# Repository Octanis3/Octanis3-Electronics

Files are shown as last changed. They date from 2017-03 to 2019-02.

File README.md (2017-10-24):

# Octanis3-Electronics

Contains PCB files of the Owl Monitoring Device. More information on http://nestbox.octanis.org/

## Folders
* *_admin*: General administrative documents (e.g. Sponsoring documents, Project proposals etc.)
* *Nestbox_v1*: First PCB version with Lighbarrier, 13MHz RFID, (untested) LORA module
* *Nextbox_v2*: Second PCB version using 125-134 kHz RFID

## Dependencies
* Created with KiCAD 4.0.4 stable
* BOM created with bom2groupedCsv.xsl plugin by Wolf Walter.
* Schematic parts managed with https://github.com/BPJWES/KiCAD_Partslist_editor

2017

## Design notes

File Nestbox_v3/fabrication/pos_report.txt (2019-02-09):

Info: Front side (top side) place file: '/Users/raffael/Desktop/Octanis/Octanis3/pcb/Nestbox_v2/fabrication/Nestbox_v2-top.pos'.
Info: Component count: 82.
Info: Back side (bottom side) place file: '/Users/raffael/Desktop/Octanis/Octanis3/pcb/Nestbox_v2/fabrication/Nestbox_v2-bottom.pos'.
Info: Component count: 4.
Info: Full component count: 86

Component Placement File generation OK.

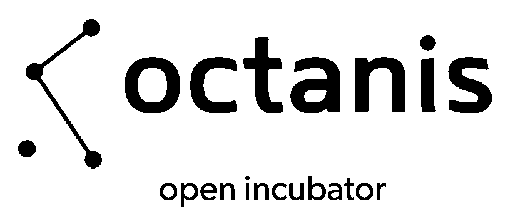
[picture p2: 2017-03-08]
_admin/octanis.bmp

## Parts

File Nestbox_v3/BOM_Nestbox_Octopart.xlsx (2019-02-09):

Item | Qty | Reference(s) | Value | LibPart | Footprint | SKU | NOTES
13 | 1 | CON301 | DEV-13712 | conn:Micro_SD_Card | Octanis3:MICRO-SD9+4P-SMD-16.1X14.5X1.85MM
14 | 1 | D301 | SMD-LED-CLEAR-YELLOW_0603_ | Nestbox_v2-cache:SMD-LED-CLEAR-GREEN_0603_ | SeeedOPL-LED-2016:LED-0603 | 304090043
15 | 1 | D302 | SMD-LED-CLEAR-BLUE_0603_ | Nestbox_v2-cache:SMD-LED-CLEAR-BLUE_0603_ | SeeedOPL-LED-2016:LED-0603 | 304090045
27 | 1 | L201 | 4.7uH | device:L | Inductors:Inductor_Taiyo-Yuden_NR-60xx_HandSoldering |  | consolidate with other inductor possible?
28 | 1 | L202 | 5uH | device:L | Inductors:Inductor_Taiyo-Yuden_NR-30xx |  | ??? Are the component names inverted???
29 | 1 | L301 | SMD-FERRITE-BEAD-2500R-50MA_0603_ | Nestbox_v2-cache:SMD-FERRITE-BEAD-2500R-50MA_0603_ | SeeedOPL-Inductor-2016:L0603 | 303030020
33 | 1 | Q201 | tph1r712mdl1q | device:Q_PMOS_DGS | Octanis3:TDSON-8-1_HandSoldering
34 | 2 | Q301, Q501 | NTR3A052PZT1G | device:Q_PMOS_GSD | TO_SOT_Packages_SMD:TSOT-23
35 | 2 | Q601, Q603 | DMG2301L-7 | device:Q_PMOS_GSD | TO_SOT_Packages_SMD:TSOT-23
36 | 2 | Q602, Q604 | DMG3402L | device:Q_NMOS_GSD | TO_SOT_Packages_SMD:TSOT-23
37 | 1 | Q701 | DMG3402L | device:Q_NMOS_GSD | TO_SOT_Packages_SMD:TSOT-23
56 | 1 | U201 | TPS62745 | Octanis3:TPS62745 | Octanis3:WSON_3x2mm_12pin |  | inductor too close.. Pads of tps not accessible
57 | 1 | U202 | LTC3534 | Octanis3:LTC3534 | SeeedOPL-IC-2016:SSOP16-0.635-5X4MM
58 | 1 | U203 | LP5907 | regul:LD3985M | texasinstruments:SOT23-5
59 | 1 | U301 | MSP430FR5969 | Octanis3:MSP430FR5969 | chips:S-PVQFN-N48
60 | 1 | U501 | ESP-12S | Octanis3:ESP-12S | Octanis3:ESP-12E_SMD_UART_ONLY
61 | 1 | U601 | ADS1220 | adc-dac:ADS1120-PW | Housings_SSOP:TSSOP-16_4.4x5mm_Pitch0.65mm
62 | 1 | Y301 | Crystal | device:Crystal | SeeedOPL-Crystal Oscillator-2016:X2-SMD-L2.0X1.2X0.55MM
 |  |  | SD CARD

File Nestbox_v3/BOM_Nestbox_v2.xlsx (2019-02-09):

Source: | /Users/raffael/Desktop/Octanis/Octanis3/pcb/Nestbox_v2/Nestbox_v2.sch
Date: | 2018 June 07, Thursday 10:21:40
Tool: | Eeschema 4.0.7
Generator: | /usr/local/Cellar/kicad/HEAD-19d5cc7/kicad.app/Contents/SharedSupport/plugins/bom_csv_grouped_by_value.py
Component Count: | 106
Item | Qty | Reference(s) | Value | LibPart | Footprint | Datasheet | MFG_PN | MFR_PN | MPN | Mouser-Part | SKU | NOTES
1 | 7 | C201, C203, C205, C206, C207, C304, C610 | 10u | device:C | Capacitors_SMD:C_0603 |  |  |  |  |  |  | Change to 805 size
2 | 5 | C202, C204, C601, C607, C608 | 1u | device:C | Capacitors_SMD:C_0603
3 | 1 | C208 | 330p | device:C | Capacitors_SMD:C_0603
4 | 1 | C209 | 10p | device:C | Capacitors_SMD:C_0603
5 | 1 | C210 | 33p | device:C | Capacitors_SMD:C_0603
6 | 4 | C301, C305, C308, C609 | 100n | device:C | Capacitors_SMD:C_0603
7 | 2 | C302, C303 | 25 pF | Nestbox_v2-cache:CERAMIC-12PF-50V-5%-NPO_0603_ | Capacitors_SMD:C_0603 |  |  |  | CC0603JRNPO9BN120 |  | 302010067 | rename; wrong MPN, is not in würth box. Used 24pf
8 | 1 | C306 | 100u | device:CP | Capacitors_SMD:C_0603 |  |  |  |  | 667-ECE-A0JKA101
9 | 1 | C307 | 0.1u | device:C | Capacitors_SMD:C_0603 |  |  |  |  |  |  | $
10 | 3 | C602, C603, C605 | 100n 1% | device:C | Capacitors_SMD:C_0603 |  |  |  |  |  |  | C602 label confusing position
11 | 2 | C604, C606 | 10n X2Y | Octanis3:C_X2Y | Octanis3:Capacitor_X2Y_603 |  |  |  |  |  |  | check land pattern with datasheet
12 | 1 | C611 | 10n | device:C | Capacitors_SMD:C_0603 |  |  |  |  |  |  | silkscreen illegible
13 | 1 | CON301 | Micro_SD_Card | conn:Micro_SD_Card | Octanis3:MICRO-SD9+4P-SMD-16.1X14.5X1.85MM
14 | 1 | D301 | SMD-LED-CLEAR-YELLOW_0603_ | Nestbox_v2-cache:SMD-LED-CLEAR-GREEN_0603_ | SeeedOPL-LED-2016:LED-0603 |  |  |  | 19-217-G7C-AN1P2-3T |  | 304090043
15 | 1 | D302 | SMD-LED-CLEAR-BLUE_0603_ | Nestbox_v2-cache:SMD-LED-CLEAR-BLUE_0603_ | SeeedOPL-LED-2016:LED-0603 |  |  |  | 19-217-BHC-ZL1M2RY-3T |  | 304090045
16 | 1 | J201 | BATT_CONN_01X02 | conn:CONN_01X02 | Terminal_Blocks:TerminalBlock_Pheonix_PT-3.5mm_2pol
17 | 1 | J401 | LB_DETECT_CONN_01X04 | conn:CONN_01X04 | Terminal_Blocks:TerminalBlock_Pheonix_MPT-2.54mm_4pol
18 | 1 | J402 | CONN_01X05 | conn:CONN_01X05 | Terminal_Blocks:TerminalBlock_Pheonix_MPT-2.54mm_5pol
19 | 1 | J501 | CONN_01X01 | conn:CONN_01X01 | Pin_Headers:Pin_Header_Straight_1x01_Pitch2.54mm
20 | 1 | J502 | CONN_01X06 | conn:CONN_01X06 | Pin_Headers:Pin_Header_Straight_1x06_Pitch2.54mm
21 | 1 | J601 | LOAD_CELL_CONN_01X04 | conn:CONN_01X04 | Terminal_Blocks:TerminalBlock_Pheonix_MPT-2.54mm_4pol
22 | 1 | J701 | RFID_CONN_01X05 | conn:CONN_01X05 | Terminal_Blocks:TerminalBlock_Pheonix_MPT-2.54mm_5pol
23 | 1 | JP201 | VAA_Jumper_SELECT_Dual | Octanis3:Jumper_SELECT_Dual | Pin_Headers:Pin_Header_Straight_1x03
24 | 1 | JP203 | Jumper_3V3 | device:Jumper | Pin_Headers:Pin_Header_Straight_1x02
25 | 1 | JP501 | Jumper | device:Jumper | Connect:GS2
26 | 1 | JP701 | V_RFID_Jumper_SELECT_Dual | Octanis3:Jumper_SELECT_Dual | Pin_Headers:Pin_Header_Straight_1x03_Pitch2.54mm
27 | 1 | L201 | 4.7uH | device:L | Inductors:Inductor_Taiyo-Yuden_NR-60xx_HandSoldering |  | XFL3010-472MEB
28 | 1 | L202 | 5uH | device:L | Inductors:Inductor_Taiyo-Yuden_NR-30xx |  |  | MSS7341-502NLD |  |  |  | ??? Are the component names inverted???
29 | 1 | L301 | SMD-FERRITE-BEAD-2500R-50MA_0603_ | Nestbox_v2-cache:SMD-FERRITE-BEAD-2500R-50MA_0603_ | SeeedOPL-Inductor-2016:L0603 |  |  |  |  |  | 303030020
30 | 1 | P301 | RX/TX | conn:CONN_01X02 | Socket_Strips:Socket_Strip_Straight_1x02_Pitch2.54mm
31 | 1 | P302 | TST/RST | conn:CONN_01X02 | Socket_Strips:Socket_Strip_Straight_1x02_Pitch2.54mm
32 | 1 | P303 | DEBUG_3V3 | conn:CONN_01X02 | Socket_Strips:Socket_Strip_Straight_1x02_Pitch2.54mm
33 | 1 | Q201 | tph1r712mdl1q | device:Q_PMOS_DGS | Octanis3:TDSON-8-1_HandSoldering
34 | 2 | Q301, Q501 | NTR3A052PZT1G | device:Q_PMOS_GSD | TO_SOT_Packages_SMD:TSOT-23
35 | 2 | Q601, Q603 | DMG2301L-7 | device:Q_PMOS_GSD | TO_SOT_Packages_SMD:TSOT-23
36 | 2 | Q602, Q604 | DMG3402L | device:Q_NMOS_GSD | TO_SOT_Packages_SMD:TSOT-23
37 | 1 | Q701 | DMG3402L | device:Q_NMOS_GSD | TO_SOT_Packages_SMD:TSOT-23
38 | 1 | R201 | 82k 1% | device:R | Resistors_SMD:R_0603 |  |  |  |  |  |  | consolidate
39 | 2 | R202, R701 | 47K 1% | device:R | Resistors_SMD:R_0603 |  |  |  |  |  |  | R701 could be 82k
40 | 1 | R203 | 10k | device:R | Resistors_SMD:R_0603
41 | 1 | R204 | 162k 1% | device:R | Resistors_SMD:R_0603
42 | 1 | R205 | 649k 1% | device:R | Resistors_SMD:R_0603
43 | 1 | R206 | 15k | device:R | Resistors_SMD:R_0603
44 | 1 | R301 | 47K | Nestbox_v2-cache:DIP-RES-47K-5%-1_4W_PR-D2.3XL6.5MM_ | Resistors_SMD:R_0603 |  |  |  | FHCFR-1_4W-473J |  | 301020022 | consolidate
45 | 6 | R303, R304, R305, R610, R611, R612 | 47R | device:R | Resistors_SMD:R_0603
46 | 2 | R306, R307 | 1K | device:R | Resistors_SMD:R_0603
47 | 8 | R308, R309, R501, R502, R503, R504, R505, R506 | 10K | device:R | Resistors_SMD:R_0603 |  |  |  |  |  |  | rename --> 10k
48 | 4 | R401, R402, R403, R404 | DNP | device:R | Resistors_SMD:R_0603
49 | 4 | R601, R602, R603, R604 | 1k 0.1% | device:R | Resistors_SMD:R_0603 |  |  |  | ERJ-PB3B1001V
50 | 2 | R605, R606 | 100R 1% | device:R | Resistors_SMD:R_0603 |  |  |  | ERA3AEB101V
51 | 2 | R607, R608 | 0R | device:R | Resistors_SMD:R_0603
52 | 1 | R609 | 2k2 | device:R | Resistors_SMD:R_0603 |  |  |  |  |  |  | could maybe be consolidated with LED resistor values
53 | 2 | R702, R703 | 47K 1% | device:R | Resistors_SMD:R_0603
54 | 2 | R704, R705 | 82k 1% | device:R | Resistors_SMD:R_0603
55 | 1 | SW301 | SMD-BUTTON_2P-3.0X2.5X1.2+0.4MM_ | Nestbox_v2-cache:SMD-BUTTON_2P-3.0X2.5X1.2+0.4MM_ | Buttons_Switches_SMD:SW_SPST_B3S-1000 |  |  |  | B3U-1000P-B |  | 311020047
56 | 1 | U201 | TPS62745 | Octanis3:TPS62745 | Octanis3:WSON_3x2mm_12pin |  |  |  |  |  |  | inductor too close.. Pads of tps not accessible
57 | 1 | U202 | LTC3534 | Octanis3:LTC3534 | SeeedOPL-IC-2016:SSOP16-0.635-5X4MM
58 | 1 | U203 | LP5907 | regul:LD3985M | texasinstruments:SOT23-5
59 | 1 | U301 | MSP430FR5969 | Octanis3:MSP430FR5969 | chips:S-PVQFN-N48 |  |  |  | MSP430FR5969IRGZR
60 | 1 | U501 | ESP-12S | Octanis3:ESP-12S | Octanis3:ESP-12E_SMD_UART_ONLY
61 | 1 | U601 | ADS1220 | adc-dac:ADS1120-PW | Housings_SSOP:TSSOP-16_4.4x5mm_Pitch0.65mm
62 | 1 | Y301 | Crystal | device:Crystal | SeeedOPL-Crystal Oscillator-2016:X2-SMD-L2.0X1.2X0.55MM |  |  |  | FC-12M 32.7680KA-A3
 |  |  |  |  |  |  |  |  | ECS-.327-12.5-12-TR
 |  |  | SD CARD |  |  |  |  |  | SDSDQAB-008G

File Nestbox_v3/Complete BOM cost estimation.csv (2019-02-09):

Qty | Line Item | Total Qty (@ Batch Size: 40) | Unit Price (@ Batch Size: 40) | Supplier | Total per device | Batch Total
 |  |  | Mouser
3 | C0805C102JAGACTU, | 120 | 0.1617 | Mouser | 0.49 | 19.40
2 | DMG2301L-7 | 80 | 0.2093 | Mouser | 0.42 | 16.75
1 | C0805C100KBRACTU, | 40 | 0.2619 | Mouser | 0.26 | 10.48
2 | DMG3402L-7 | 80 | 0.2748 | Mouser | 0.55 | 21.98
1 | DMG3402L-7 | 40 | 0.2748 | Mouser | 0.27 | 10.99
1 | C0805C182JAGACAUTO | 40 | 0.2778 | Mouser | 0.28 | 11.11
1 | C0805C152JBGACAUTO | 40 | 0.2788 | Mouser | 0.28 | 11.15
2 | NTR3A052PZT1G | 80 | 0.3085 | Mouser | 0.62 | 24.68
1 | LP5907MFX-3.0/NOPB | 40 | 0.4464 | Mouser | 0.45 | 17.86
1 | FC-12M 32.7680KA-A3 | 40 | 0.5704 | Mouser | 0.57 | 22.82
1 | MSS7341-502NLB | 40 | 1.2897 | Mouser | 1.29 | 51.59
1 | tph1r712mdl1q | 40 | 1.4286 | Mouser | 1.43 | 57.14
1 | XFL3010-472MEB | 40 | 1.7163 | Mouser | 1.72 | 68.65
1 | TPS62745DSSR | 40 | 1.7262 | Mouser | 1.73 | 69.05
1 | MSP430FR5969IRGZR | 40 | 4.1667 | Mouser | 4.17 | 166.67
1 | LTC3534EDHC#PBF | 40 | 6.2599 | Mouser | 6.26 | 250.40
1 | SDSDQAB-008G | 40 | 6.8948 | Mouser | 6.89 | 275.79
1 | ADS1220IPW | 40 | 8.8988 | Mouser | 8.90 | 355.95
1 | DEV-13712 | 40 | 14.8314 | Mouser | 14.83 | 593.25
1 | Passive Parts | 40 |  |  | 10.00 | 400.00
 |  | Total component value |  |  | 61.39 | 2455.72
 |  | SeeedStudio Markup (10%) |  |  | 6.14 | 245.57
 | Total component price (Seeedstudio) |  |  |  | 67.53 | 2701.29
1 | Wifi ESP-12S | 40 |  |  | 3.97 | 158.73
1 | YGX-SP3 | 40 |  | Alibaba | 22.00 | 880.00
2 | SensorCable | 80 |  | AliExpress | 9.00 | 360.00
1 | SonoffCase | 40 |  | AliExpress | 5.16 | 206.35
1 | EM4095HMSO16A | 40 |  |  | 3.00 | 120.00
1 | RFID Coil | 40 |  | Priority1Design | 5.50 | 220.20
1 | RFID Case | 40 |  | Aliexpress | 0.85 | 34.13
1 | AABatteryCase | 40 |  | Aliexpress | 1.03 | 41.27
1 | Nestbox PCB | 40 |  |  | 3.97 | 158.73
1 | RFID PCB | 40 |  |  | 2.98 | 119.05
1 | Mechanical Parts | 40 |  |  | 10.00 | 400.00
1 | Wood, MDF, LaserCutter | 40 |  |  | 5.00 | 200.00
1 | User Button | 40 |  |  | 0.99 | 39.68
1 | 4pc Battery LADDA | 40 |  | IKEA | 6.95 | 278.00
1 | PCB assembly | 40 |  |  | 39.68 | 1587.30
 | Total other parts value |  |  |  | 120.09 | 4803.43
 | VAT import fees (7.7%) |  |  |  | 9.25 | 369.86
 | Other import service fees, shipping and tariffs |  |  |  |  | 500.00
 | Total costs for electronics |  |  |  | 209.36 | 8374.59

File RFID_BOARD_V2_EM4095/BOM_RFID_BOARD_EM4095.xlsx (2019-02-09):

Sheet: RFID_BOARD_EM4095.csv
Source: | /Users/raffael/Desktop/Octanis/Octanis3/pcb/RFID_BOARD_V2_EM4095/RFID_BOARD_EM4095.sch
Date: | 2018 July 01, Sunday 18:29:10
Tool: | Eeschema 4.0.7
Generator: | /usr/local/Cellar/kicad/HEAD-19d5cc7/kicad.app/Contents/SharedSupport/plugins/bom_csv_grouped_by_value.py
Component Count: | 25
Individual Components:
Item | Qty | Reference(s) | Value | LibPart | Footprint | Datasheet | MPN
 |  | C1 | 10u | device:C | Capacitors_SMD:C_0805
 |  | C2 | 100n | device:C | Capacitors_SMD:C_0603
 |  | C3 | 1.8n 250V | device:C | Capacitors_SMD:C_0805 |  | C0805C182JAGAC
 |  | C4 | 1.8n 250V | device:C | Capacitors_SMD:C_0805 |  | C0805C182JAGAC
 |  | C5 | 10n (22n max) | device:C | Capacitors_SMD:C_0603
 |  | C6 | 10n | device:C | Capacitors_SMD:C_0603
 |  | C7 | 100n | device:C | Capacitors_SMD:C_0603
 |  | C8 | DNP or 100n | device:C | Capacitors_SMD:C_0603 | DNP
 |  | C9 | 100n 250V | device:C | Capacitors_SMD:C_0603
 |  | C10 | 100n 250V | device:C | Capacitors_SMD:C_0603
 |  | C11 | 100n | device:C | Capacitors_SMD:C_0603
 |  | C12 | 10u | device:C | Capacitors_SMD:C_0805
 |  | CRES1 | C_fine_tuning (10nF, 50V) | device:C | Capacitors_SMD:C_0603
 |  | CRES2 | 1.8n 250V | device:C | Capacitors_SMD:C_0805 |  | C0805C182JAGAC
 |  | CRES3 | 1n 450V | device:C | Capacitors_SMD:C_0805 |  | C0805C102JAGACTU or CC0805JKNPOBBN102
 |  | Cdiv1 | 10p 500V | device:C | Capacitors_SMD:C_0805 |  | C0805C100KBRACTU
 |  | Cdiv2 | 1.5n | device:C | Capacitors_SMD:C_0603
 |  | D1 | STTH1R06 | device:D | Diodes_SMD:SMB_Standard
 |  | J1 | CONN_01X05 | conn:CONN_01X05 | Pin_Headers:Pin_Header_Straight_1x05_Pitch2.54mm
 |  | J2 | CONN_01X01 | conn:CONN_01X01 | Measurement_Points:Measurement_Point_Square-SMD-Pad_Small
 |  | J3 | CONN_01X01 | conn:CONN_01X01 | Measurement_Points:Measurement_Point_Square-SMD-Pad_Small
 |  | R1 | 100R | device:R | Resistors_SMD:R_0603
 |  | R2 | 100k | device:R | Resistors_SMD:R_0603
 |  | R3 | 0R | device:R | Resistors_SMD:R_0603
 |  | U1 | EM4095 | Octanis3:EM4095 | Housings_SOIC:SOIC-16_3.9x9.9mm_Pitch1.27mm
Collated Components:
Item | Qty | Reference(s) | Value | LibPart | Footprint | Datasheet | MPN | assembly notes
1 | 2 | C1, C12 | 10u | device:C | Capacitors_SMD:C_0805 |  |  | c1 c11 part value exchanged
2 | 4 | C2, C7, C8, C11 | 100n | device:C | Capacitors_SMD:C_0603 |  |  | C8 must be precise! The rest is decoupling
3 | 3 | C3, C4, CRES2 | 1.8n 250V | device:C | Capacitors_SMD:C_0805 |  | C0805C182JAGAC
4 | 2 | C5, C6 | 10n | device:C | Capacitors_SMD:C_0603 |  |  | C5 can be max. 22n
8 | 1 | CRES1 | C_fine_tuning (10nF, 50V) | device:C | Capacitors_SMD:C_0603 |  |  | placed 10n from würth --> Target frequency ca. 124-125 kHz
7 | 2 | C9, C10 | 100n 250V | device:C | Capacitors_SMD:C_0603 |  | C2012X7T2E104K125AA | should be 0805 footprint!!!
9 | 1 | CRES3 | 1n 450V | device:C | Capacitors_SMD:C_0805 |  | C0805C102JAGACTU or CC0805JKNPOBBN102
10 | 1 | Cdiv1 | 10p 500V | device:C | Capacitors_SMD:C_0805 |  | C0805C100KBRACTU
11 | 1 | Cdiv2 | 1.5n | device:C | Capacitors_SMD:C_0603 |  | C0805C152JBGACAUTO
12 | 1 | D1 | STTH1R06 | device:D | Diodes_SMD:SMB_Standard
15 | 1 | R1 | 100R | device:R | Resistors_SMD:R_0603
16 | 1 | R2 | 100k | device:R | Resistors_SMD:R_0603
17 | 1 | R3 | 0R | device:R | Resistors_SMD:R_0603
2 left!!! | 1 | U1 | EM4095 | Octanis3:EM4095 | Housings_SOIC:SOIC-16_3.9x9.9mm_Pitch1.27mm

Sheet: FINAL VERSION
Item | Qty | Reference(s) | Value | LibPart | Footprint | Datasheet | MPN | assembly notes |  | capacitor choice (nF)
1 | 2 | C1, C12 | 10u | device:C | Capacitors_SMD:C_0805 |  | GRM21BR61E106MA73L |  | Inductor value | 2.8 | 2.56 | 2.56 | 2.56 | 2.56
2 | 4 | C2, C7, C8, C11 | 100n | device:C | Capacitors_SMD:C_0603 |  | GCM188L81H104KA57D | C8 must be precise! The rest is decoupling | res3 | 1 | 1 | 1.1 | 1 | 1
 |  | C8 | 100n 1%
3 | 1 | CRES2 | 1.8n 250V | device:C | Capacitors_SMD:C_0805 |  | C0805C182JAGAC |  | res2 | 1.8 | 1.8 | 1.6 | 1.8 | 1.8
4 | 2 | C5, C6 | 10n | device:C | Capacitors_SMD:C_0603 |  | CGA3E1C0G2A103J080AC | C5 can be max. 22n, alternative: GRM1885C1H103JA01D | res1 | 10 | 10 | 10 | 15 | 68
5 | 1 | CRES1 | 12nF | device:C | Capacitors_SMD:C_0603 |  | VJ0603Y153JXAAC (https://www.mouser.ch/ProductDetail/Vishay-Vitramon/VJ0603Y153JXAAC?qs=sGAEpiMZZMs0AnBnWHyRQKubRBCdVSJlEvhtpSFB550%3d) | 15n alternative: VJ0603Y153JXAAC | f_res (kHz) | 122.3807176 | 127.9888181 | 127.1564094 | 126.6937883 | 124.6482345
6 | 1 | CRES3 | 1n 450V | device:C | Capacitors_SMD:C_0805 |  | CC0805JKNPOBBN102 | (C0805C102JAGACTU or CC0805JKNPOBBN102)
7 | 1 | Cdiv1 | 10p 500V | device:C | Capacitors_SMD:C_0805 |  | C0805C100KBRACTU
8 | 1 | Cdiv2 | 1.5n | device:C | Capacitors_SMD:C_0603 |  | C0805C152JBGACAUTO
9 | 1 | R3 | 0R | device:R | Resistors_SMD:R_0603
10 | 1 | U1 | EM4095 | Octanis3:EM4095 | Housings_SOIC:SOIC-16_3.9x9.9mm_Pitch1.27mm

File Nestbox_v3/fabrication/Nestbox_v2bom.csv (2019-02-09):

Id | Designator | Package | Quantity | Designation | Supplier and ref
1 | FID3,FID2,FID1 | Fiducial_1mm_Dia_2.54mm_Outer_CopperTop | 3 | Fiducial_1mm_Dia_2.54mm_Outer_CopperTop
2 | R304,R303,R305,R610,R611,R612 | R_0603 | 6 | 47R
3 | REF**,REF**,REF** | MountingHole_2.5mm | 3 | MountingHole_2.5mm
4 | C201,C203,C205,C206,C207,C304,C610 | C_0603 | 7 | 10u
5 | C202,C204,C601,C607,C608 | C_0603 | 5 | 1u
6 | C301,C305,C308,C609 | C_0603 | 4 | 100n
7 | C302,C303 | C_0603 | 2 | 25 pF
8 | C306 | C_0603 | 1 | 100u
9 | C307 | C_0603 | 1 | 0.1u
10 | C602,C603,C605 | C_0603 | 3 | 100n 1%
11 | C611 | C_0603 | 1 | 10n
12 | D301 | LED-0603 | 1 | SMD-LED-CLEAR-GREEN_0603_
13 | D302 | LED-0603 | 1 | SMD-LED-CLEAR-BLUE_0603_
14 | J201 | TerminalBlock_Pheonix_PT-3.5mm_2pol | 1 | BATT_CONN_01X02
15 | JP203 | Pin_Header_Straight_1x02 | 1 | Jumper_3V3
16 | JP701 | Pin_Header_Straight_1x03_Pitch2.54mm | 1 | V_RFID_Jumper_SELECT_Dual
17 | L301 | L0603 | 1 | SMD-FERRITE-BEAD-2500R-50MA_0603_
18 | P301 | Socket_Strip_Straight_1x02_Pitch2.54mm | 1 | RX/TX
19 | P302 | Socket_Strip_Straight_1x02_Pitch2.54mm | 1 | TST/RST
20 | R201 | R_0603 | 1 | 100k
21 | R202,R701 | R_0603 | 2 | 50k
22 | R203 | R_0603 | 1 | 10k
23 | R204 | R_0603 | 1 | 162k
24 | R205 | R_0603 | 1 | 649k
25 | R301 | R_0603 | 1 | 47K
26 | R306,R307 | R_0603 | 2 | 1K
27 | R308,R309,R501,R502,R503,R504,R505,R506 | R_0603 | 8 | 10K
28 | R601,R602,R603,R604 | R_0603 | 4 | 1k 1%
29 | R605,R606 | R_0603 | 2 | 100R 1%
30 | R607,R608 | R_0603 | 2 | 0R
31 | R609 | R_0603 | 1 | 2k2
32 | R702,R703 | R_0603 | 2 | 18k
33 | R704,R705 | R_0603 | 2 | 33k
34 | SW301 | SW_SPST_B3S-1000 | 1 | SMD-BUTTON_2P-3.0X2.5X1.2+0.4MM_
35 | U203 | SOT23-5 | 1 | LP5907
36 | U301 | S-PVQFN-N48 | 1 | MSP430FR5969
37 | U601 | TSSOP-16_4.4x5mm_Pitch0.65mm | 1 | ADS1220
38 | Y301 | X2-SMD-L2.0X1.2X0.55MM | 1 | Crystal
39 | JP201 | Pin_Header_Straight_1x03 | 1 | VAA_Jumper_SELECT_Dual
40 | P303 | Socket_Strip_Straight_1x02_Pitch2.54mm | 1 | DEBUG_3V3
41 | C208 | C_0603 | 1 | 330p
42 | C209 | C_0603 | 1 | 10p
43 | C210 | C_0603 | 1 | 33p
44 | L201 | Inductor_Taiyo-Yuden_NR-60xx_HandSoldering | 1 | 4.7uH
45 | L202 | Inductor_Taiyo-Yuden_NR-30xx | 1 | 5uH
46 | R206 | R_0603 | 1 | 15k
47 | U202 | SSOP16-0.635-5X4MM | 1 | LTC3534
48 | J501 | Pin_Header_Straight_1x01_Pitch2.54mm | 1 | CONN_01X01
49 | R401,R402,R403,R404 | R_0603 | 4 | DNP
50 | J401 | TerminalBlock_Pheonix_MPT-2.54mm_4pol | 1 | LB_DETECT_CONN_01X04
51 | J402 | TerminalBlock_Pheonix_MPT-2.54mm_5pol | 1 | CONN_01X05
52 | J601 | TerminalBlock_Pheonix_MPT-2.54mm_4pol | 1 | LOAD_CELL_CONN_01X04
53 | J701 | TerminalBlock_Pheonix_MPT-2.54mm_5pol | 1 | RFID_CONN_01X05
54 | J502 | Pin_Header_Straight_1x06_Pitch2.54mm | 1 | CONN_01X06
55 | Q601,Q603 | TSOT-23 | 2 | DMG2301L-7
56 | U501 | ESP-12E_SMD_UART_ONLY | 1 | ESP-12S
57 | Q602,Q604 | TSOT-23 | 2 | DMG3402L
58 | JP501 | GS2 | 1 | Jumper
59 | C604,C606 | Capacitor_X2Y_603 | 2 | 10n X2Y
60 | Q201 | TDSON-8-1_HandSoldering | 1 | Q_PMOS_DGS
61 | CON301 | MICRO-SD9+4P-SMD-16.1X14.5X1.85MM | 1 | Micro_SD_Card
62 | U201 | WSON_3x2mm_12pin | 1 | TPS62745
63 | G*** | octanis3_logo | 1 | LOGO
64 | G*** | VogelwarteLogo3 | 1 | LOGO
65 | G*** | octanis_open_incubator_logo | 1 | LOGO
66 | REF*** | OSHW-Logo2_9.8x8mm_SilkScreen | 1 | OSHW-Logo2_9.8x8mm_SilkScreen
67 | Q301,Q501 | TSOT-23 | 2 | NTR3A052PZT1G
68 | Q701 | TSOT-23 | 1 | Q_NMOS_GSD

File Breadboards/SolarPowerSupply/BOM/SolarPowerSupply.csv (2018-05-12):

Reference | Quantity | Value | Footprint | Datasheet | MPN | Tolerance
BT101 | 1 | Battery | Octanis3:TE_282834-2 |  | 571-282834-2
C101 | 1 | 4.7u | Octanis3:C_SMD_2012_Hand |  | 81-GRM21R61A475KE34D | 10%
C102 | 1 | 100n | Capacitors_SMD:C_0603_HandSoldering
C103 | 1 | 10n | Capacitors_SMD:C_0603_HandSoldering |  |  | 10%
C104 C105 C106 C107 C108 C109 | 6 | 10u | Octanis3:C_SMD_2012_Hand |  | 81-GRM21BR61C106KE5K
C110 | 1 | 10p | Capacitors_SMD:C_0603_HandSoldering
D101 D102 | 2 | LED | LEDs:LED_0603_HandSoldering
JP101 JP102 JP103 JP104 JP105 | 5 | Jumper | Pin_Headers:Pin_Header_Straight_1x02_Pitch2.54mm
L101 | 1 | 22u | Inductors_SMD:L_Wuerth_WE-TPC-3816 |  | 710-744031220 | 20%
L102 L103 | 2 | 1.5u | Octanis3:L_2520_HandSoldering |  | 81-1269AS-H-1R5MP2
P101 | 1 | CONN_01X04 | Pin_Headers:Pin_Header_Straight_1x04_Pitch2.54mm
P102 | 1 | CONN_01X07 | Pin_Headers:Pin_Header_Straight_1x07_Pitch2.54mm
R101 | 1 | 1.69M | Resistors_SMD:R_0603_HandSoldering |  | 71-CRCW06031M69FKEA | 1%
R102 | 1 | 0.576M | Resistors_SMD:R_0603_HandSoldering |  | 71-CRCW0603-576K-E3 | 1%
R103 | 1 | 9.09M | Resistors_SMD:R_0603_HandSoldering |  | 71-CRCW06039M09FKEA | 1%
R104 | 1 | 6.04M | Resistors_SMD:R_0603_HandSoldering |  | 71-CRCW06036M04FKEA | 1%
R105 R114 R115 | 3 | 5.36M | Resistors_SMD:R_0603_HandSoldering |  | 71-CRCW06035M36FKEA | 1%
R106 | 1 | 5.9M | Resistors_SMD:R_0603_HandSoldering |  | 71-CRCW06035M90FKEA | 1%
R107 | 1 | 0E | Resistors_SMD:R_1206_HandSoldering
R108 | 1 | 4.12M | Resistors_SMD:R_0603_HandSoldering |  | 71-CRCW06034M12FKEA | 1%
R109 | 1 | 4.42M | Resistors_SMD:R_0603_HandSoldering |  | 71-CRCW06034M42FKEA | 1%
R110 | 1 | 3.65M | Resistors_SMD:R_0603_HandSoldering |  | 71-CRCW0603-3.65M-E3 | 1%
R111 R112 | 2 | 4.53M | Resistors_SMD:R_0603_HandSoldering |  | 71-CRCW06034M53FKEA | 1%
R113 | 1 | 0E | Resistors_SMD:R_0603_HandSoldering
R116 | 1 | DNP | Resistors_SMD:R_0603_HandSoldering
R117 R118 | 2 | R | Resistors_SMD:R_0603_HandSoldering
R119 R120 | 2 | 1M | Resistors_SMD:R_0603_HandSoldering |  | 71-CRCW06031M10JNEA
R121 | 1 | 1.1M | Resistors_SMD:R_0603_HandSoldering |  | 71-CRCW06031M10JNEA | 1%
R122 | 1 | 205k | Resistors_SMD:R_0603_HandSoldering |  | 71-CRCW0603-205K-E3 | 1%
SC101 | 1 | Solar_Cells | Octanis3:TE_282834-2 |  | 571-282834-2
U101 | 1 | bq25504 | Housings_DFN_QFN:QFN-16-1EP_3x3mm_Pitch0.5mm |  | 595-BQ25504RGTT
U102 | 1 | TPS63051 | Octanis3:VQFN_12_2.5x2.5mm |  | 595-TPS63051RMWT
U103 | 1 | TPS63050 | Octanis3:VQFN_12_2.5x2.5mm |  | 595-TPS63050RMWR

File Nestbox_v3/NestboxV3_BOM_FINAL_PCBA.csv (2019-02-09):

Reference(s) | MPN | Qty | MouserLink
C201, C203, C205, C206, C207, C304, C610 | CC0805KKX5R8BB106 | 7
C202, C204, C601, C607, C608 | CC0603KRX7R8BB105 | 5
C208 | CC0603JRNPO9BN331 | 1
C209 | CC0603JRNPO9BN100 | 1
C210 | CC0603JRNPO9BN330 | 1
C301, C305, C307, C308, C609 | CC0603KRX7R9BB104 | 5
C302, C303 | CC0603JRNPO9BN250 | 2 | https://www.mouser.ch/ProductDetail/Yageo/CC0603JRNPO9BN250
C306 | 293D107X0016D2TE3 | 1
C602, C603 | CC0603JRX7R7BB104 | 2
C611 | CC0603KRX7R9BB103 | 1
D301 | 19-217-G7C-AN1P2-3T | 1
D302 | 19-217-BHC-ZL1M2RY-3T | 1
L201 | MSS7341-502NLD | 1
L202 | XFL3010-472MEB | 1
L301 | BLM18AG121SN1D | 1
Q201 | TPH1R712MDL1Q | 1 | https://www.mouser.ch/ProductDetail/Toshiba/TPH1R712MDL1Q
Q301, Q501 | NTR3A052PZT1G | 2
Q701 | DMG3402L-7 | 1
R201, R207, R208, R302, R507, R701, R704, R705 | RC0603FR-0782KL | 8
R202, R702, R703 | RC0603FR-0747KL | 3
R203, R308, R309, R501, R503, R504, R505, R506 | RC0603JR-0710KL | 8
R204 | RC0603FR-07162KL | 1
R205 | RC0603FR-07649KL | 1
R206 | RC0603JR-0715KL | 1
R301 | RC0603FR-0747KL | 1
R303, R304, R603, R604 | RC0603JR-070RL | 4
R306, R307 | RC0603FR-071KL | 2
R605, R606 | RC0603FR-07100RL | 2
R610, R611, R612 | RC0603JR-0747RL | 3
SW301 | DTSM-62K-S-V-T/R(SN431) | 1
U201 | TPS62745DSSR | 1
U202 | LTC3534EDHC#PBF | 1
U203 | LP5907MFX-3.0/NOPB | 1
U301 | MSP430FR5969IRGZR | 1
U501 | ESP-12F | 1
U601 | ADS1220IPW | 1
Y301 | FC-12M 32.7680KA-A3 | 1

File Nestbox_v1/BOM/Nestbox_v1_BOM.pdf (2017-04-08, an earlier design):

Reference | Quantity | Value | Footprint
ANT_UHF1 | | 1 ANTENNA-CONN-U-FL_3P_ | SeeedOPL-Connector-2016:U-FL3P-SMD-2.6X2.6X1.0MM
BT1 | | 1 Battery | Connectors_Molex:Molex_KK-6410-02_02x2.54mm_Straight
C10 C14 | | 2 CERAMIC-1UF-25V-10%-X7R_0603_ | SeeedOPL-Capacitor-2016:C0603
C12 C13 | | 2 180pF | SeeedOPL-Capacitor-2016:C0603
C15 C16 | | 2 DNP | SeeedOPL-Capacitor-2016:C0603
C11 C17 | | 2 CERAMIC-10NF-50V-10%-X7R_0603_ | SeeedOPL-Capacitor-2016:C0603
C19 C22 | | 2 82pF | SeeedOPL-Capacitor-2016:C0402
C20 C21 C25 | | 3 DNP | Capacitors_SMD:C_0603
C23 C24 | | 2 150 pF | Capacitors_SMD:C_0603
C27 C28 | | 2 CERAMIC-22UF-6.3V-20%-X5R_0805_ | SeeedOPL-Capacitor-2016:C0805
C2 C3 | | 2 CERAMIC-12PF-50V-5%-NPO_0603_ | SeeedOPL-Capacitor-2016:C0603
C26 C4 | | 2 CERAMIC-10UF-25V-10%-X5R_0805_ | SeeedOPL-Capacitor-2016:C0805
C1 C18 C29 C5 C9 | | 5 CERAMIC-100NF-50V-10%-X7R_0603_ | SeeedOPL-Capacitor-2016:C0603
C6 C8 | | 2 CERAMIC-10PF-50V-5%-NPO_0603_ | SeeedOPL-Capacitor-2016:C0603
C7 | | 1 CERAMIC-1NF-50V-10%-X7R_0603_ | SeeedOPL-Capacitor-2016:C0603
D1 | | 1 SFH 4646 | Octanis3:MIDLED
D2 | | 1 SMD-LED-CLEAR-GREEN_0603_ | SeeedOPL-LED-2016:LED-0603
D3 | | 1 SMD-LED-CLEAR-BLUE_0603_ | SeeedOPL-LED-2016:LED-0603
FI1 | | 1 NFM18PS105R0J3D | murata-filter:NFM18PS
JP1 JP2 | | 2 JUMPER | Socket_Strips:Socket_Strip_Straight_1x02
L1 | 1 SMD-FERRITE-BEAD-2500R-50MA_0603_ SeeedOPL-Inductor-2016:L0603
L2 L5 | 2 | 742792042 Resistors_SMD:R_0805
L3 L4 | | 2 560nH | Resistors_SMD:R_0805
L6 | 1 | 742792093 Resistors_SMD:R_0805
L7 | | 1 XFL4020-102ME | Octanis3:XFL4020
P1 | | 1 RX/TX | Socket_Strips:Socket_Strip_Straight_1x02
P2 | | 1 TST/RST | Socket_Strips:Socket_Strip_Straight_1x02
P3 | | 1 VDD/GND | Socket_Strips:Socket_Strip_Straight_1x02
P4 | | 1 NFC_PWR_SEL | Socket_Strips:Socket_Strip_Straight_1x03
PB1 | | 1 LIGHT_BARRIER1 | Socket_Strips:Socket_Strip_Straight_1x02
PB2 | | 1 LIGHT_BARRIER2 | Socket_Strips:Socket_Strip_Straight_1x02
Q1 Q2 | | 2 SFH 3605 | Octanis3:MIDLED_phototransistor
R1 | | 1 SMD-RES-220R-5%-1_10W_0603_
R10 R13 R14 R18 | | 4 SMD-RES-0R-5%-1_10W_0603_ | SeeedOPL-Resistor-2016:R0603
R12 R15 R17 R2 R23 R28 R29 R3 R4 R9 | | 10 DNP | Resistors_SMD:R_0603
R11 R16 R19 R20 R8 | | 5 SMD-RES-3.3K-1%-1_10W_0603_ | SeeedOPL-Resistor-2016:R0603
R21 R22 | | 2 SMD-RES-330R-1%-1_10W_0603_ | SeeedOPL-Resistor-2016:R0603
R24 | | 1 SMD-RES-560K-5%-1_10W_0603_ | SeeedOPL-Resistor-2016:R0603
R25 | | 1 180k | Resistors_SMD:R_0603
R27 | | 1 47K | SeeedOPL-Resistor-2016:R0603
R5 R6 | | 2 SMD-RES-1K-5%-1_10W_0603_ | SeeedOPL-Resistor-2016:R0603
R26 R30 R7 | | 3 SMD-RES-10K-1%-1_10W_0603_ | SeeedOPL-Resistor-2016:R0603
RV1 RV2 | | 2 POT:2K | pot:3223G
SW1 | 1 SMD-BUTTON_2P-3.0X2.5X1.2+0.4MM_ SeeedOPL-Switch-2016:SW2-2.6-3.0X2.5X1.2+0.4MM
U1 | | 1 MSP430FR5969 | chips:S-PVQFN-N48
U2 | | 1 ST95HF | Octanis3:VFQFPN32
U3 | | 1 TPS630250RNC | Octanis3:RNC0014A
U4 | | 1 RN2483 | Octanis3:RN2483
Y1 | | 1 Crystal | SeeedOPL-Crystal Oscillator-2016:X2-SMD-L2.0X1.2X0.55MM
Y2 | | 1 ABM11-142-27.120MHz | Octanis3:Crystal_ABM11-142
ant1 | | 1 NFC_antenna | Octanis3:NFC_ANTENNA_CIRC

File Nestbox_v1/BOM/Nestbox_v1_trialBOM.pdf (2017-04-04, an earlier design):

Reference | Value | Footprint | MPN | SKU
D1 | SFH 4646 | Octanis3:MIDLED | 720-SFH4646Z
R1 | 100 Ohm, but also try higher values | SeeedOPL-Resistor-2016:R0603 | RC0603JR-07100RL | 301010090
R2 | DNP | Resistors_SMD:R_0603
Q1 | SFH 3605 | Octanis3:MIDLED_phototransistor | SFH 3605-Z
R4 | DNP | Resistors_SMD:R_0603
RV1 | 2k Trimmer | pot:3223G | 3313J-1-201E
R3 | DNP | Resistors_SMD:R_0603
Q2 | SFH 3605 | Octanis3:MIDLED_phototransistor | SFH 3605-Z
R28 | DNP | Resistors_SMD:R_0603
RV2 | 2k Trimmer or higher | pot:3223G | 3313J-1-201E
R29 | DNP | Resistors_SMD:R_0603
L3 | 0 Ohm | Resistors_SMD:R_0805 | CV201210-R56K
L4 | 0 Ohm | Resistors_SMD:R_0805 | CV201210-R56K
R21 | 330 Ohm | SeeedOPL-Resistor-2016:R0603 | RC0603FR-07330RL | 301010300
R22 | 330 Ohm | SeeedOPL-Resistor-2016:R0603 | RC0603FR-07330RL | 301010300
C12 | DNP | SeeedOPL-Capacitor-2016:C0603 | CC0603JRNPO9BN101 | 302010076
C13 | DNP | SeeedOPL-Capacitor-2016:C0603 | CC0603JRNPO9BN101 | 302010076
C15 | DNP | SeeedOPL-Capacitor-2016:C0603 | CC0603JRNPO9BN101 | 302010076
C16 | DNP | SeeedOPL-Capacitor-2016:C0603 | CC0603JRNPO9BN101 | 302010076
C19 | 150pF | SeeedOPL-Capacitor-2016:C0402 | CC0402JRNPO9BN470 | 302010007
C22 | 150pF | SeeedOPL-Capacitor-2016:C0402 | CC0402JRNPO9BN470 | 302010007

## Light barrier test

## Matching network variant 1: according to guided example

C21 | DNP | Capacitors_SMD:C_0603
C20 | DNP | Capacitors_SMD:C_0603
C24 | 15 pF | Capacitors_SMD:C_0603
C25 | DNP | Capacitors_SMD:C_0603
C23 | 220 pF | Capacitors_SMD:C_0603 | GQM1875C2E820JB12D
R23 | DNP | Resistors_SMD:R_0603
ant1 | NFC_antenna | Octanis3:NFC_ANTENNA_CIRC
L3 | 560nH (part number 742792042) | Resistors_SMD:R_0805 | CV201210-R56K or 742792042)
L4 | 560nH (part number 742792042) | Resistors_SMD:R_0805 | CV201210-R56K or 742792042)
R21 | 330 Ohm | SeeedOPL-Resistor-2016:R0603 | RC0603FR-07330RL | 301010300
R22 | 330 Ohm | SeeedOPL-Resistor-2016:R0603 | RC0603FR-07330RL | 301010300
C12 | 180 pF | SeeedOPL-Capacitor-2016:C0603 | CC0603JRNPO9BN101 | 302010076
C13 | 180 pF | SeeedOPL-Capacitor-2016:C0603 | CC0603JRNPO9BN101 | 302010076
C15 | DNP | SeeedOPL-Capacitor-2016:C0603 | CC0603JRNPO9BN101 | 302010076
C16 | DNP | SeeedOPL-Capacitor-2016:C0603 | CC0603JRNPO9BN101 | 302010076
C19 | 82pF | SeeedOPL-Capacitor-2016:C0402 | CC0402JRNPO9BN470 | 302010007
C22 | 82pF | SeeedOPL-Capacitor-2016:C0402 | CC0402JRNPO9BN470 | 302010007
C21 | DNP | Capacitors_SMD:C_0603
C20 | DNP | Capacitors_SMD:C_0603
C24 | 150 pF | Capacitors_SMD:C_0603
C25 | DNP | Capacitors_SMD:C_0603
C23 | 150 pF | Capacitors_SMD:C_0603 | GQM1875C2E820JB12D
R23 | DNP | Resistors_SMD:R_0603
ant1 | NFC_antenna | Octanis3:NFC_ANTENNA_CIRC

## Matching network variant 2: similar to Demo board

"DNP" = Do not place

## Explanations

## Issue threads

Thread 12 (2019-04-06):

### ISSUE TITLE
Next version PCB

### ISSUE THREAD

**Issue by traffael** [Octanis3/Octanis3-Electronics#12]
This issue summarizes the anticipated changes to the board for the next version.

+ larger MSP430 (e.g. FR5964) with maximum possible FRAM size for longer storage periods.
+ battery monitoring possibility (i.e. analog readout of the voltage)
- remove FI1 and replace with an alternative, less fragile filter part
- larger button

**Comment by traffael** [comment]
+ change IR receiver to something like this: TSOP75338WTR (TV remote IR receiver)

**Comment by deragent** [comment]
Design of v2 of Nestbox PCB is in progress (on branch Nestbox_v2). 

Will incorporate most of these changes proposed here.

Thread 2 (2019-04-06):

### ISSUE TITLE
Assemble & Test v1 PCB

### ISSUE THREAD

**Issue by traffael** [Octanis3/Octanis3-Electronics#2]

**Comment by traffael** [comment]
Done testing:
- general microcontroller functionality/flashing/blink/...
- SPI communication between uC and RFID chip
- RFID communication (UID readout from card) with read range up to 5 cm with smartcard
- on/off IR LED and photodetector

TO DO:
- determine good intensity of IR LED and practical readout voltages of the phototransistor
- test read range with real bird ring & adjust matching network if needed
- Power supply (DC-DC converter from battery voltage to 3.3V)

In general, v1 seems to be usable for testing in the real context!

**Comment by deragent** [comment]
So after some more extended testing things do not look so good anymore:
- Light Barrier was changed to use a  TSOP38238 for the receive side. This works very stable now in our Lab tests!
- The RFID communication was implemented and worked in general, but the system is very unstable and after some time (minutes) leads to system resets. Often after these resets the RFID chip stops working altogether. It often starts working again after re-soldering it or just heating it. We do not really know the source of these problems.
- The read range using bird tags is also very disappointing when it works, being on the order of 2-3 cm within the axis of the antenna, and basically 0 cm when not in the axis of the antenna.
- The DC/DC circuit is not working correctly at the moment. Given that the design was previously used in other projects this is most likely due to assembly problems (soldering etc).

The current strategy is to make some prototypes usable just having the light-barrier and storing the passages locally.
We also started working on a v2 prototype using 125kHz RFID instead of 13.65MHz.

**Comment by traffael** [comment]
done

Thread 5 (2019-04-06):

### ISSUE TITLE
Assembly of second light barrier

### ISSUE THREAD

**Issue by traffael** [Octanis3/Octanis3-Electronics#5]
(could use the same v1 PCB and only mound phototransistor & LED and connect it to the fully mounted reader PCB)

**Comment by deragent** [comment]
I would actually propose the second light barrier directly on the same PCB but on the other side! 
So the same position as the other light barrier but just on the lower side of the PCB. In order to not get interference between the two light barriers we can also switch the diode and the transistor on one side.

Given that this version is a prototype, I think it would be a good idea to put this directly in the design. We can still add a connector and some 0-Ohm resistors to disable this second light barrier and use an external one.
But I think to detect the passing and direction of a bird the proposed solution with two barriers just next to each other should work.

**Comment by traffael** [comment]
have added a second phototransistor on the backside (it is presumably enough to have just one light source). the thickness of the PCB is probably not enough though to detect a difference in time when one or the other barrier was interrupted.

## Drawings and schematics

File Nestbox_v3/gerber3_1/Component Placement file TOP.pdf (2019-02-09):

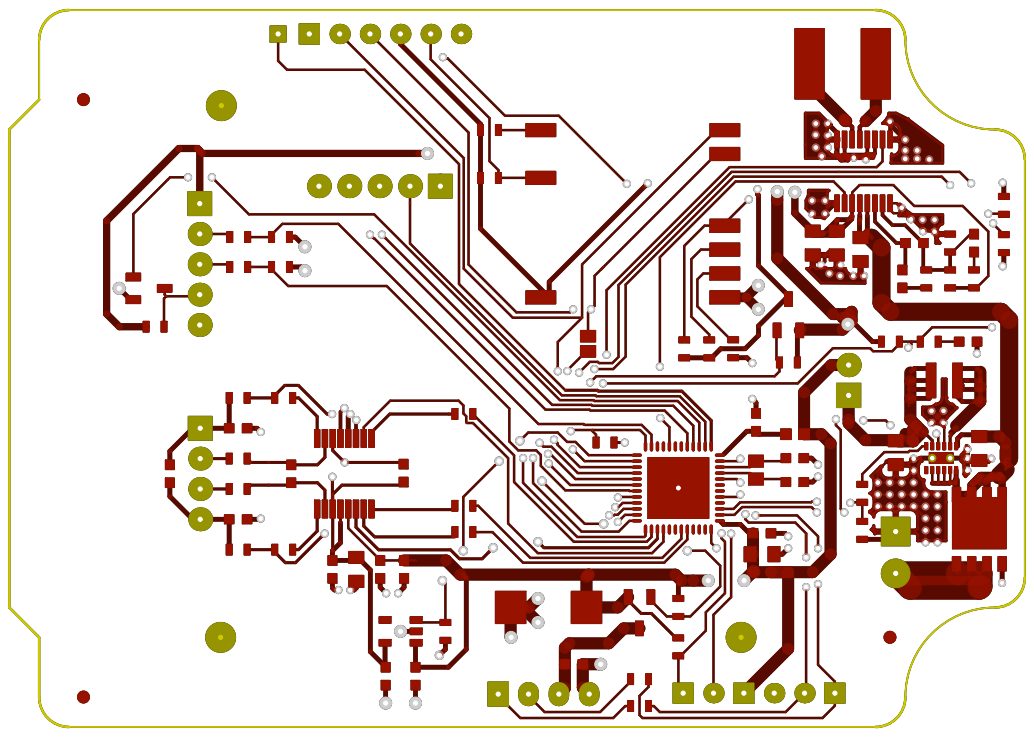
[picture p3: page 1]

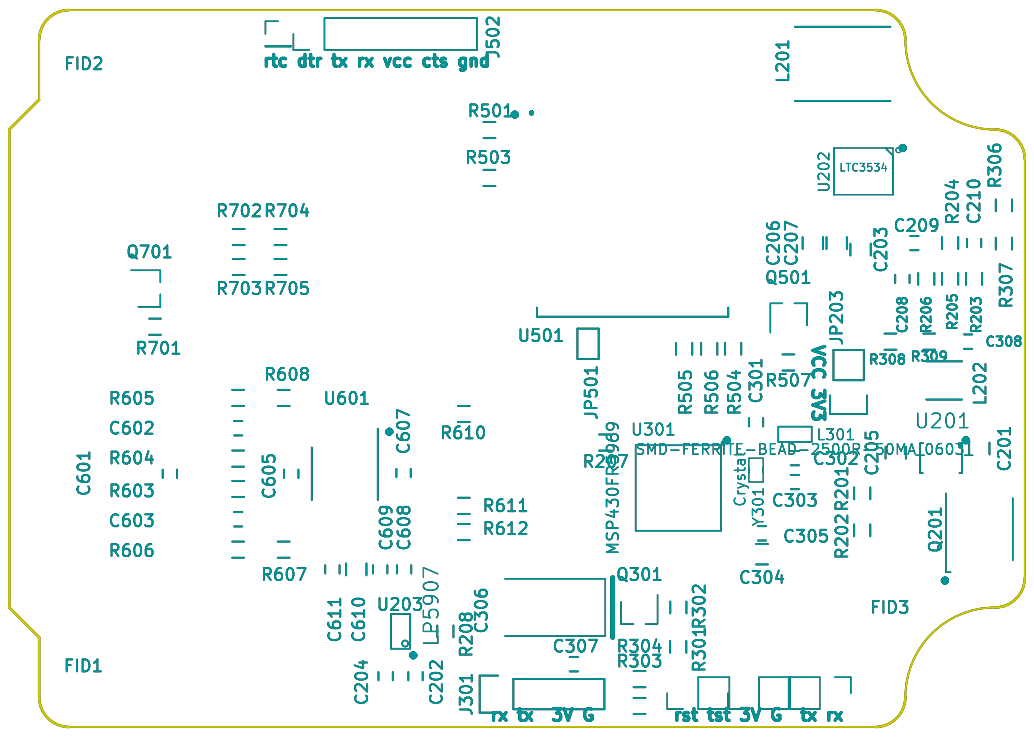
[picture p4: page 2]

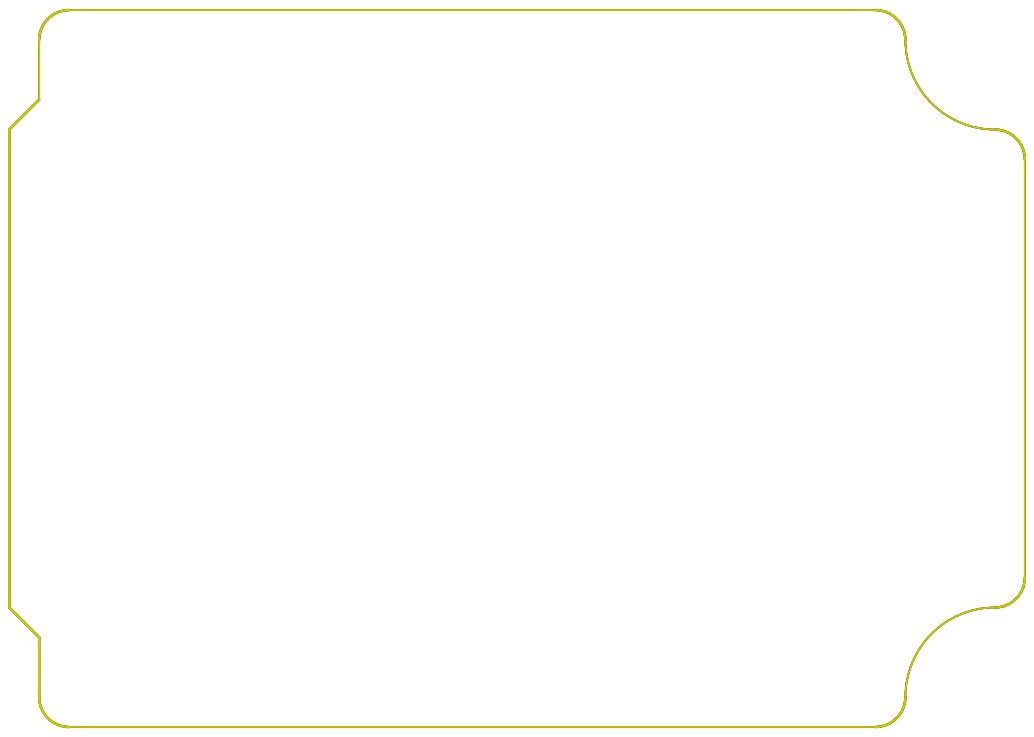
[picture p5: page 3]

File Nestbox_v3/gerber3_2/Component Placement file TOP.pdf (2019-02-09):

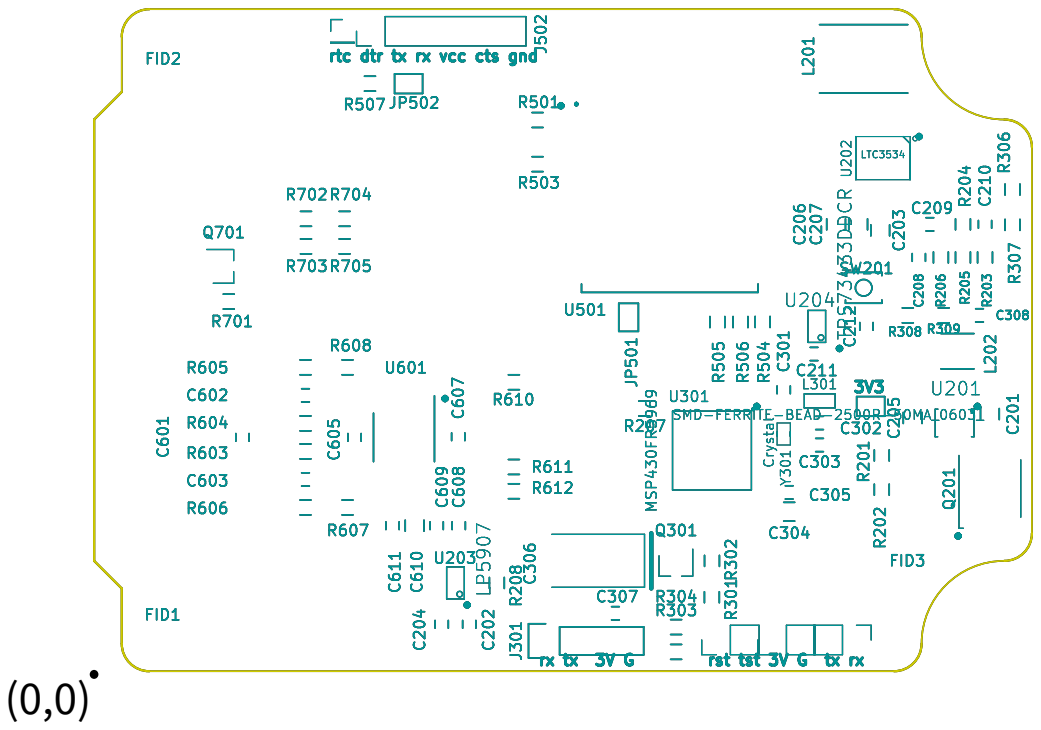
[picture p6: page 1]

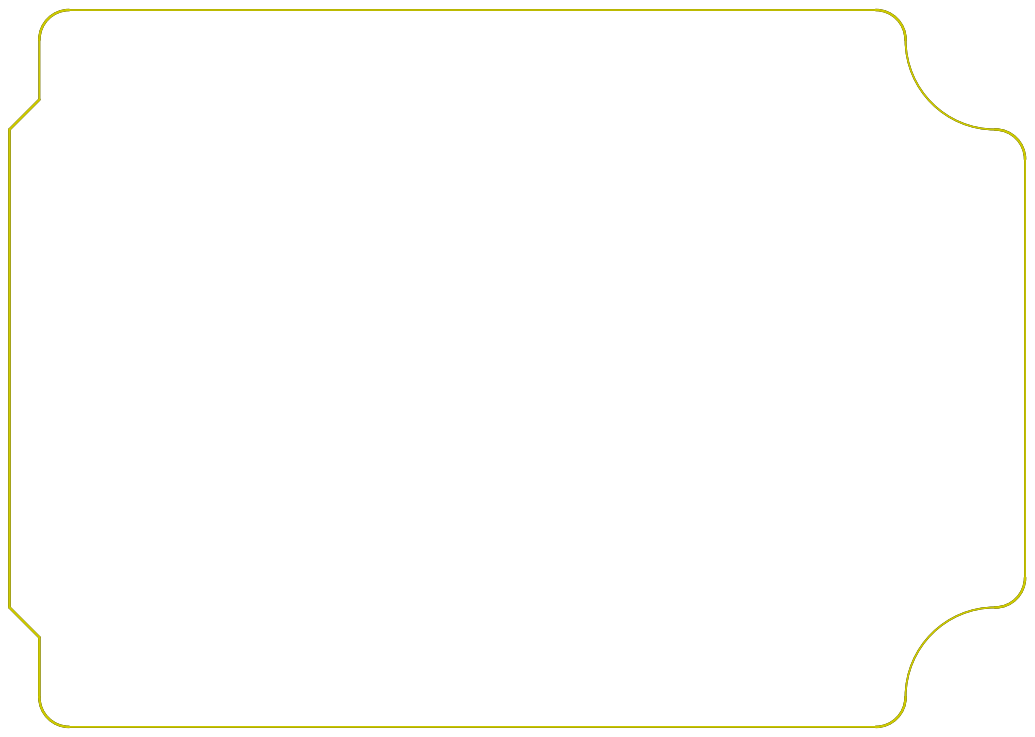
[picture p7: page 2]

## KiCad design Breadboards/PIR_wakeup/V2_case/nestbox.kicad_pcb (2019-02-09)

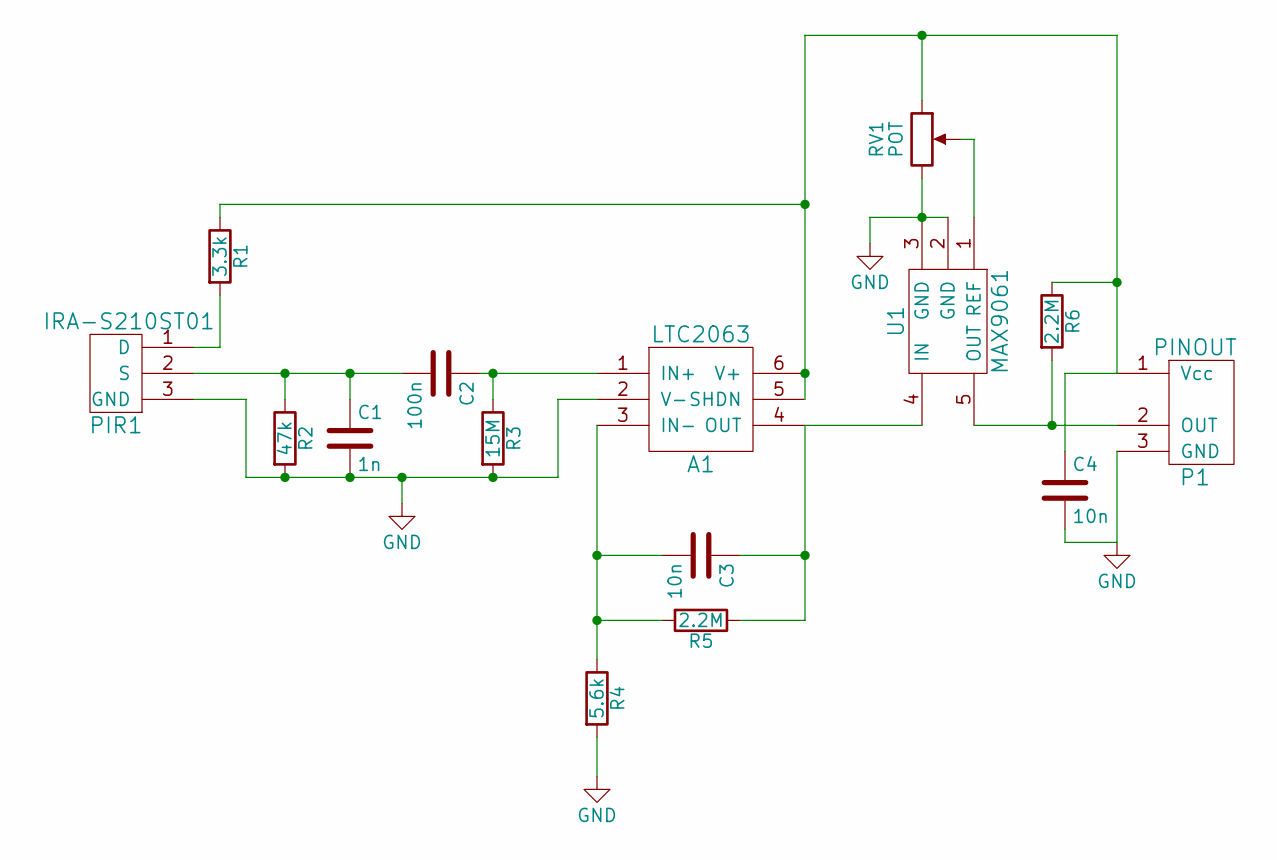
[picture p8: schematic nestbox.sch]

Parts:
A1: LTC2063; SOT-363_SC-70-6_Handsoldering
C1: 1n; C_0603_HandSoldering
C2: 100n; C_0603_HandSoldering
C3, C4: 10n; C_0603_HandSoldering
P1: PINOUT; Pin_Header_Straight_1x03_Pitch2.54mm
PIR1: IRA-S210ST01
R1: 3.3k; R_0603_HandSoldering
R2: 47k; R_0603_HandSoldering
R3: 15M; R_0603_HandSoldering
R4: 5.6k; R_0603_HandSoldering
R5, R6: 2.2M; R_0603_HandSoldering
RV1: POT; Pot
U1: MAX9061

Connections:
GND: A1.2 (V-), C1.2, C4.2, P1.3 (GND), PIR1.3 (GND), R2.2, R3.2, R4.2, RV1.3, U1.2 (GND), U1.3 (GND)
unnamed: A1.1 (IN+), C2.1, R3.1
unnamed: A1.3 (IN-), C3.2, R4.1, R5.2
unnamed: A1.4 (OUT), C3.1, R5.1, U1.4 (IN)
unnamed: A1.5 (SHDN), A1.6 (V+), C4.1, P1.1 (Vcc), R1.1, R6.1, RV1.1
unnamed: C1.1, C2.2, PIR1.2 (S), R2.1
unnamed: P1.2 (OUT), R6.2, U1.5 (OUT)
unnamed: PIR1.1 (D), R1.2
unnamed: RV1.2, U1.1 (REF)

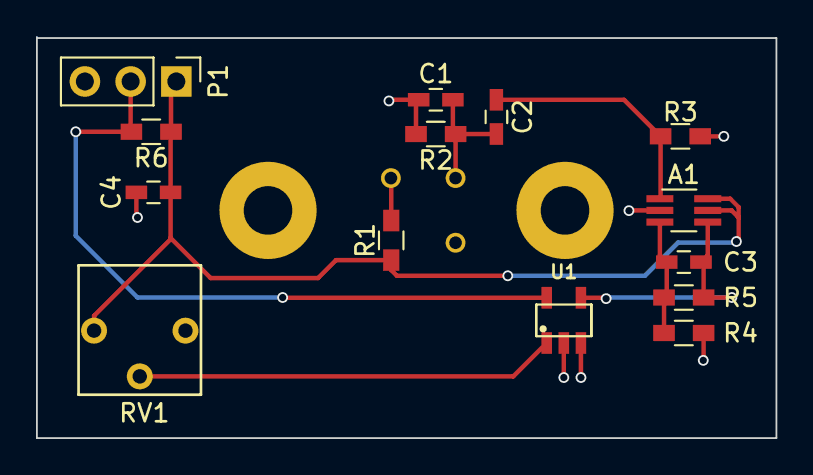
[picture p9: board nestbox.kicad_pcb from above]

Board: 2 copper layers, 41.1 x 22.3 mm, 15 parts (1 on the bottom side), 9 nets.

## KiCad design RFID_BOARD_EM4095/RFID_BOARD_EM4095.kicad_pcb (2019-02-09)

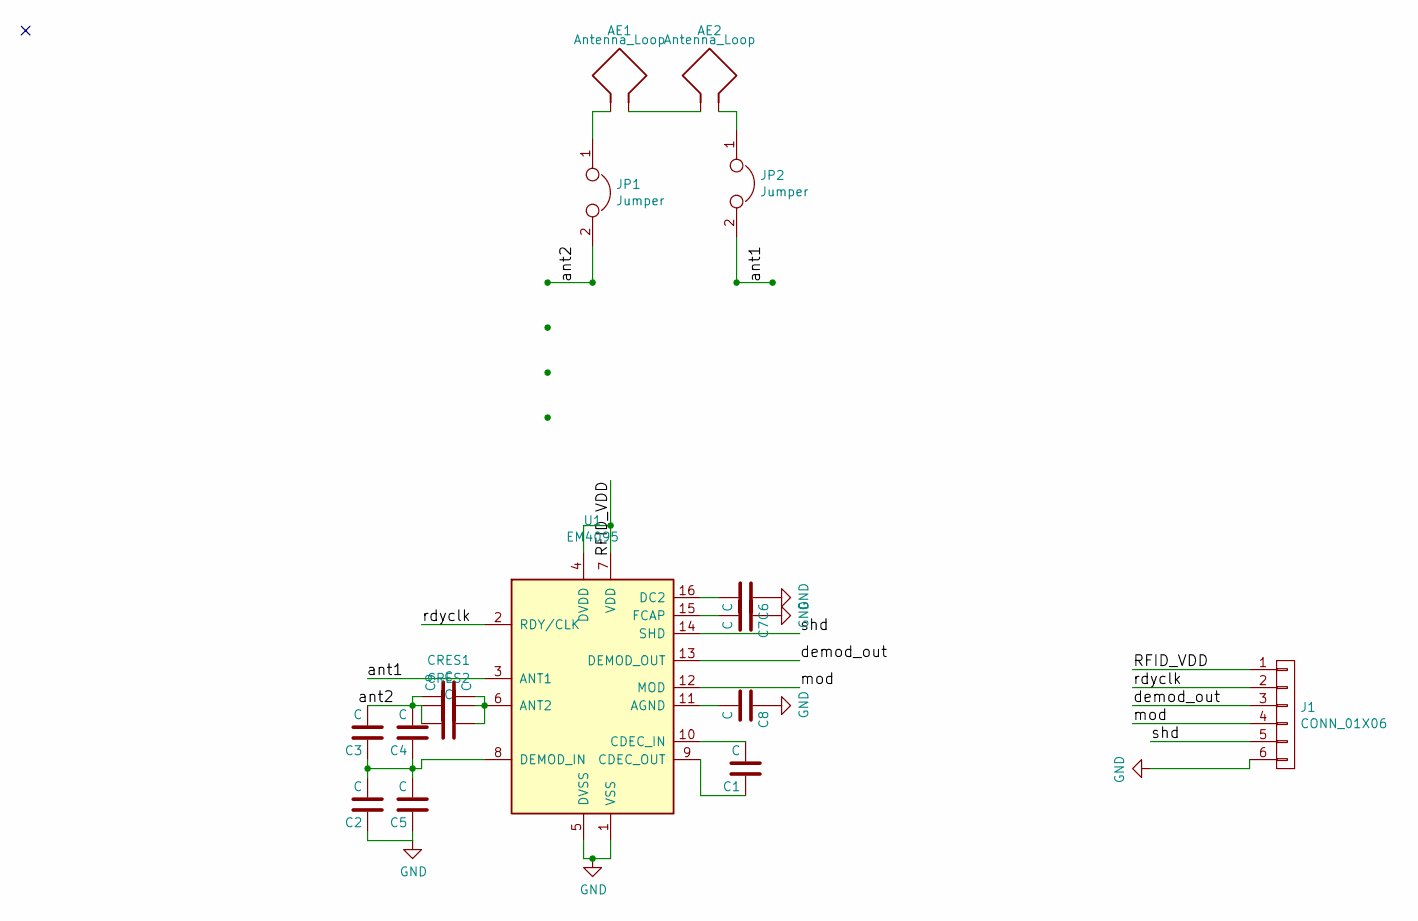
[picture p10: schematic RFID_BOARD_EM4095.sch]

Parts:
AE1, AE2: Antenna_Loop; 125kHz_PCB_Antenna
C1, C2, C3, C4, C5, C6, C7, C8, C9: C; C_0603
CRES1, CRES2: C; C_Rect_L7_W2_P5
J1: CONN_01X06; PINHEAD1-6
JP1, JP2: Jumper; Pin_Header_Straight_1x02_Pitch2.00mm
U1: EM4095; SOIC-16_3.9x9.9mm_Pitch1.27mm

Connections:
/RFID_VDD: J1.1, U1.4 (DVDD), U1.7 (VDD)
/ant1: JP2.2, U1.3 (ANT1)
/ant2: C3.2, C4.2, C9.1, CRES1.2, CRES2.2, JP1.2; also elsewhere on the board
/demod_out: J1.3, U1.13 (DEMOD_OUT)
/mod: J1.4, U1.12 (MOD)
/rdyclk: J1.2, U1.2 (RDY/CLK)
/shd: J1.5, U1.14 (SHD)
GND: C2.1, C5.1, C6.1, C7.1, C8.1, J1.6, U1.1 (VSS), U1.5 (DVSS)
unnamed: AE1.1, JP1.1
unnamed: AE1.2, AE2.2
unnamed: AE2.1, JP2.1
unnamed: C1.1, U1.9 (CDEC_OUT)
unnamed: C1.2, U1.10 (CDEC_IN)
unnamed: C2.2, C3.1, C4.1, C5.2, U1.8 (DEMOD_IN)
unnamed: C6.2, U1.16 (DC2)
unnamed: C7.2, U1.15 (FCAP)
unnamed: C8.2, U1.11 (AGND)
unnamed 17: C9.2, CRES1.1, CRES2.1, U1.6 (ANT2); also elsewhere on the board

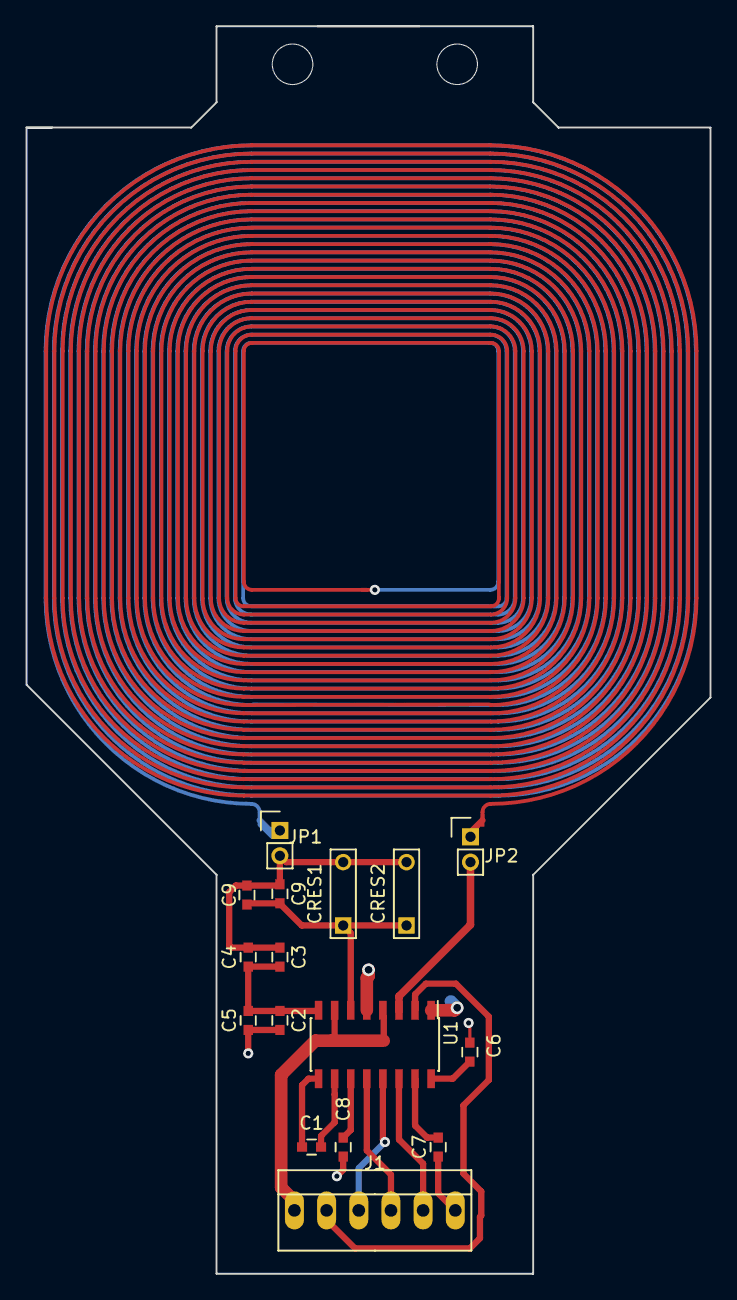
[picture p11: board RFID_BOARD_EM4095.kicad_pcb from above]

Board: 2 copper layers, 54.0 x 98.5 mm, 18 parts (1 on the bottom side), 18 nets.

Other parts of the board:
C9#2: C; C_0603

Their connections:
/ant2: C9#2.1; also elsewhere on the board
unnamed 17: C9#2.2; also elsewhere on the board

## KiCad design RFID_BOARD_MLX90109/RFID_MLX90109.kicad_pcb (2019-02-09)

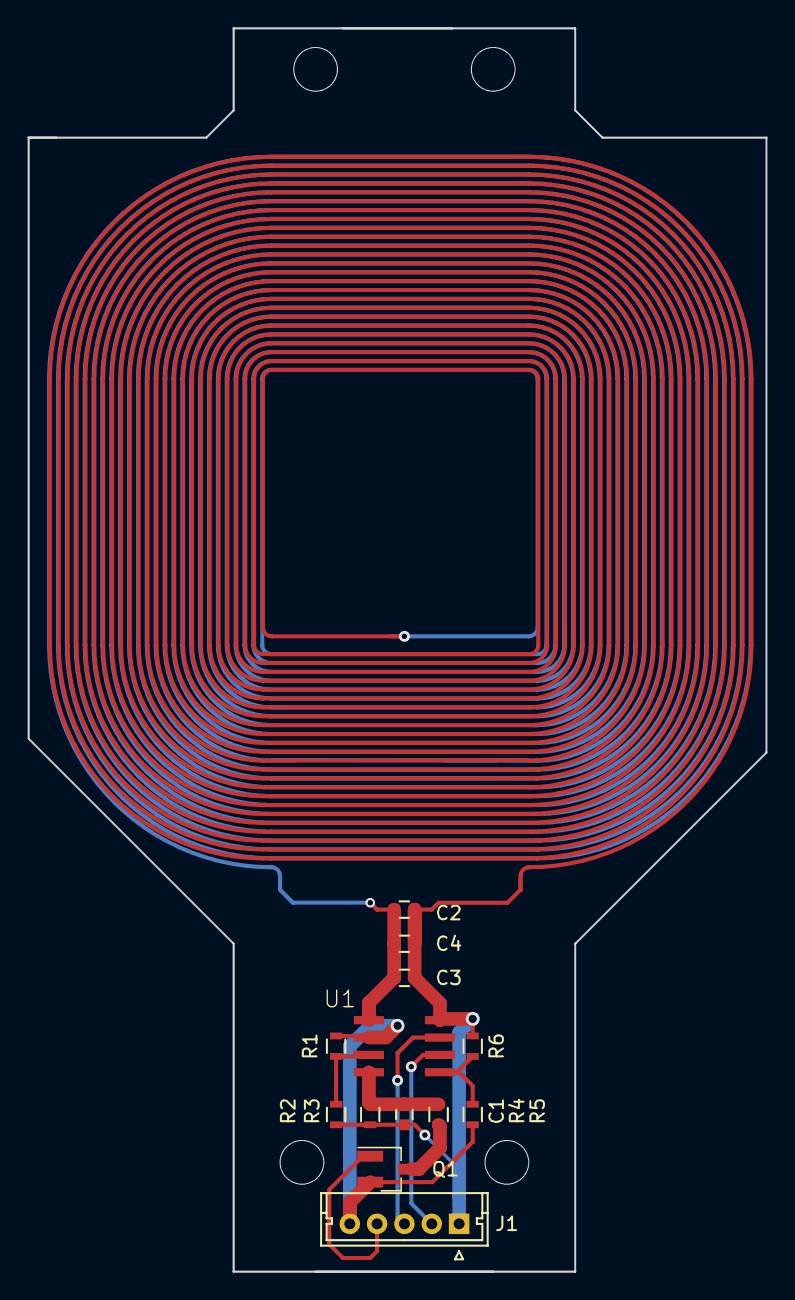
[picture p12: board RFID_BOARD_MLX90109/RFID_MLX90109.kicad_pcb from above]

Board: 2 copper layers, 54.0 x 91.0 mm, 15 parts (1 on the bottom side), 11 nets.

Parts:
AE1, AE2: Antenna_Loop; 125kHz_PCB_Antenna
C1, C2, C3, C4: C; C_0603
J1: CONN_01X05; Molex_MicroLatch-53253-0570_05x2.00mm_Straight
Q1: Q_NMOS_GSD; SOT-23_Handsoldering
R1, R2, R5, R6: R; R_0603
R3: 100k; R_0603
R4: 36k; R_0603
U1: MLX90109; SO8

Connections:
/RFID_ANT: AE1.1, C2.2, C3.2, C4.2, U1.1
/RFID_CLOCK: J1.2, U1.6
/RFID_DATA: J1.3, U1.7
/RFID_MODE: R5.2, R6.1, U1.5
/RFID_SPEED: R1.1, R2.1, U1.3
/RFID_VDD: AE2.1, C1.2, C2.1, C3.1, C4.1, J1.1, R2.2, R3.2, R6.2, U1.8
GND: J1.5, Q1.2, R1.2, R5.1, U1.2
unnamed: AE1.2, AE2.2
unnamed: C1.1, R3.1, R4.2, U1.4
unnamed: Q1.3, R4.1
RFID_MODU_N: J1.4, Q1.1

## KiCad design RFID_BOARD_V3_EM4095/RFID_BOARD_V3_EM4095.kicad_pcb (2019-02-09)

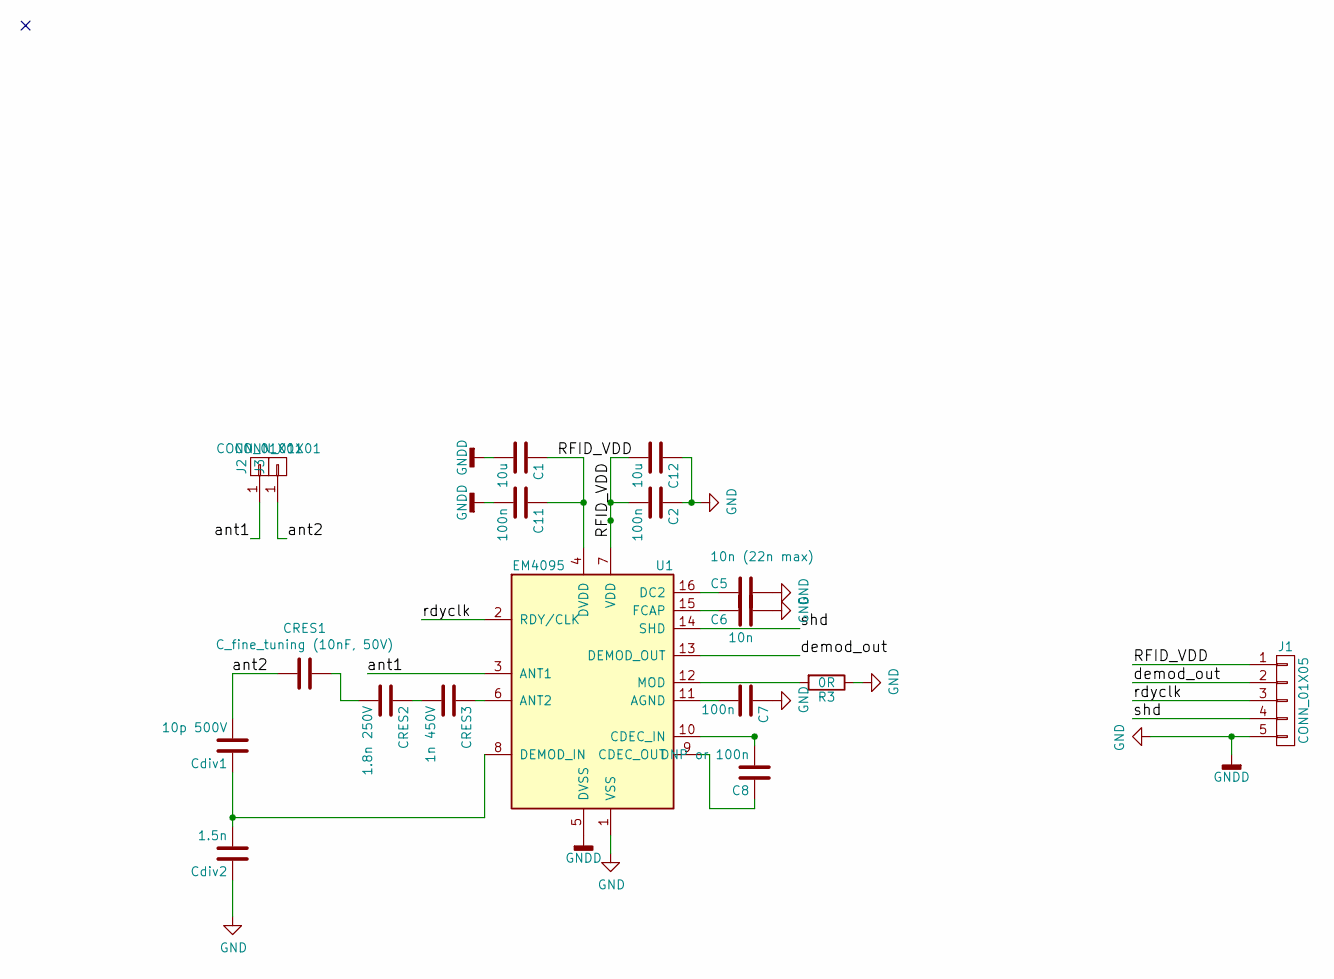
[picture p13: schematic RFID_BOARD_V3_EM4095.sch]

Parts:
C1, C12: 10u; C_0805
C2, C7, C11: 100n; C_0603
C5: 10n (22n max); C_0603
C6: 10n; C_0603
C8: DNP or 100n; C_0603
CRES1: C_fine_tuning (10nF, 50V); C_0603
CRES2: 1.8n 250V; C_0805; MPN C0805C182JAGAC
CRES3: 1n 450V; C_0805; MPN C0805C102JAGACTU or CC0805JKNPOBBN102
Cdiv1: 10p 500V; C_0805; MPN C0805C100KBRACTU
Cdiv2: 1.5n; C_0603
J1: CONN_01X05; Pin_Header_Straight_1x05_Pitch2.54mm
J2, J3: CONN_01X01; Measurement_Point_Square-SMD-Pad_Small
R3: 0R; R_0603
U1: EM4095; SOIC-16_3.9x9.9mm_Pitch1.27mm

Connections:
/RFID_VDD: C1.1, C2.2, C11.1, C12.2, J1.1, U1.4 (DVDD), U1.7 (VDD)
/ant1: J2.1, U1.3 (ANT1)
/ant2: CRES1.2, Cdiv1.2, J3.1
/demod_out: J1.2, U1.13 (DEMOD_OUT)
/rdyclk: J1.3, U1.2 (RDY/CLK)
/shd: J1.4, U1.14 (SHD)
GND: C1.2, C2.1, C5.1, C6.1, C7.1, C11.2, C12.1, Cdiv2.1, J1.5, R3.1, U1.1 (VSS), U1.5 (DVSS)
unnamed: C5.2, U1.16 (DC2)
unnamed: C6.2, U1.15 (FCAP)
unnamed: C7.2, U1.11 (AGND)
unnamed: C8.1, U1.9 (CDEC_OUT)
unnamed: C8.2, U1.10 (CDEC_IN)
unnamed: CRES1.1, CRES2.2
unnamed: CRES2.1, CRES3.2
unnamed: CRES3.1, U1.6 (ANT2)
unnamed: Cdiv1.1, Cdiv2.2, U1.8 (DEMOD_IN)
unnamed: R3.2, U1.12 (MOD)

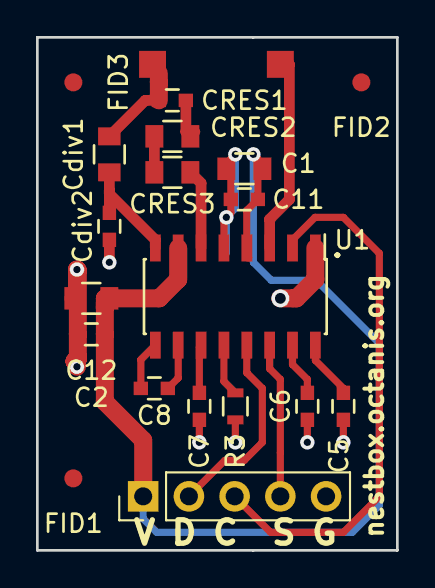
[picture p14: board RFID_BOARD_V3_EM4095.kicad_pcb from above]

Board: 2 copper layers, 20.0 x 28.5 mm, 21 parts (0 on the bottom side), 17 nets.

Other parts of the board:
FID1, FID2, FID3: Fiducial_1mm_Dia_2.54mm_Outer_CopperTop

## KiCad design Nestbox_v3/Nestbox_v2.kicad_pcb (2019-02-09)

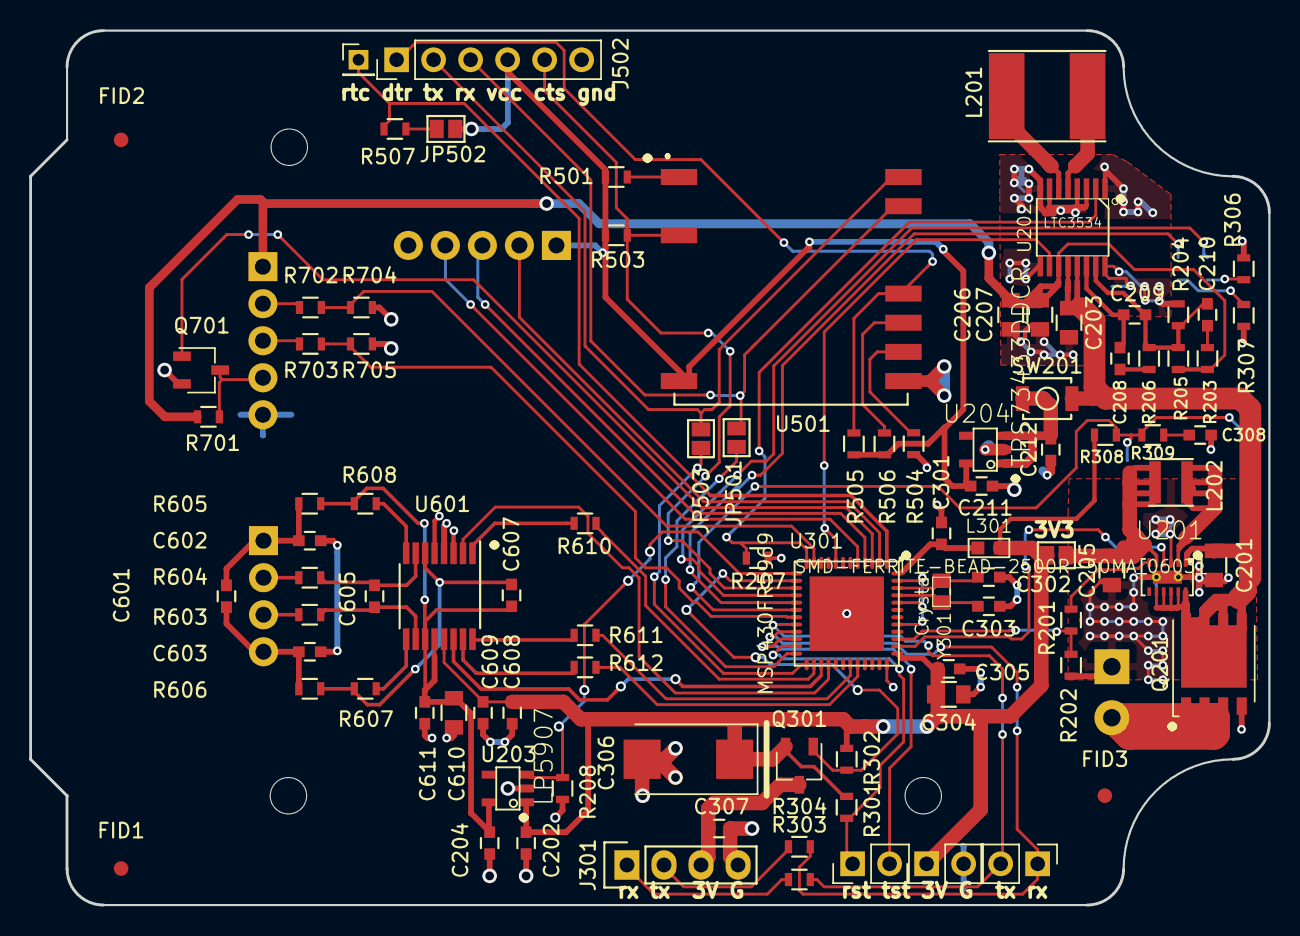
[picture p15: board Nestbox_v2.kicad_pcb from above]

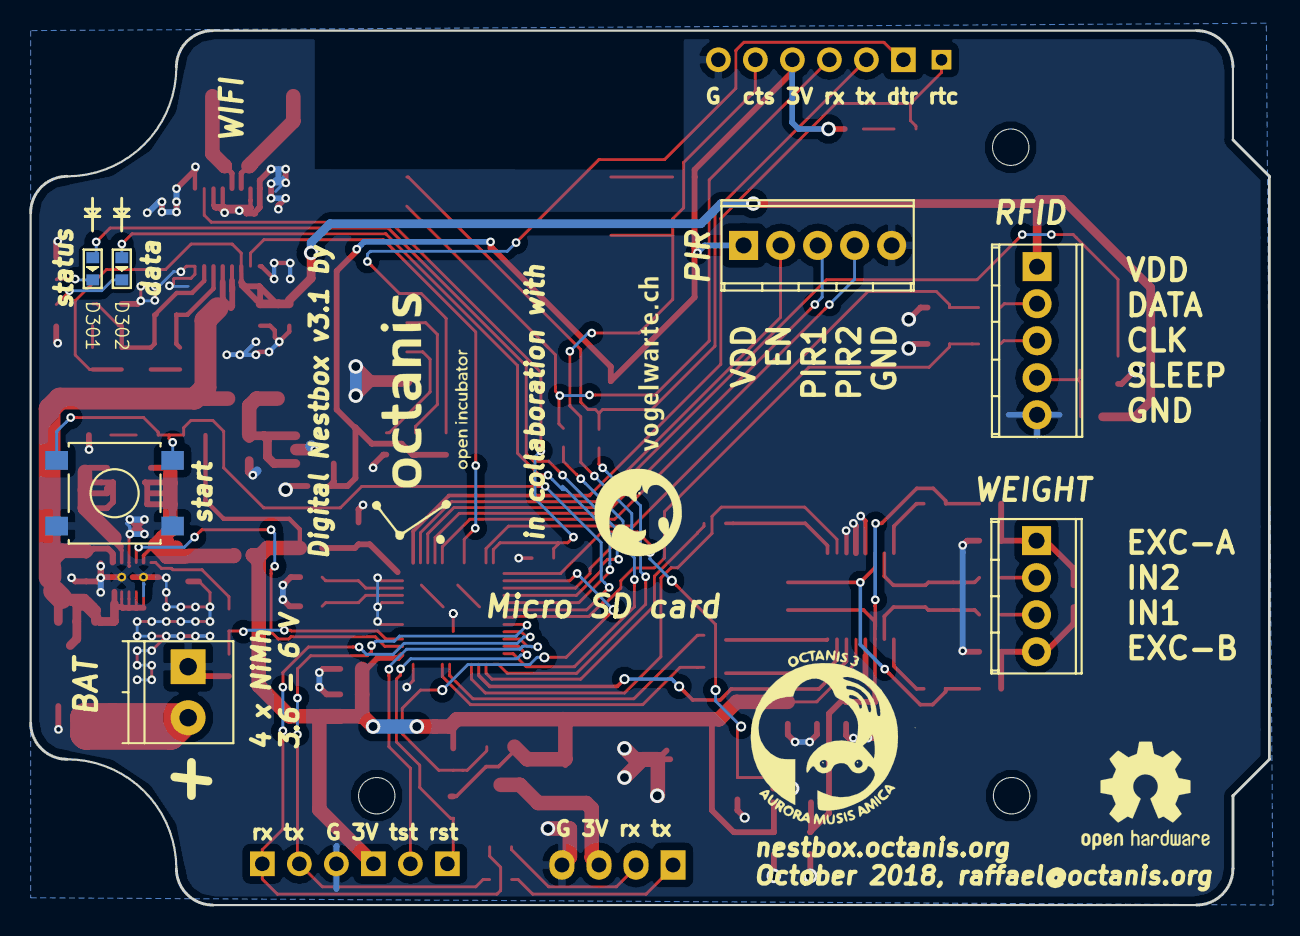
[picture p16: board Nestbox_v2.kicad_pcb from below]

Board: 2 copper layers, 85.0 x 60.0 mm, 100 parts (7 on the bottom side), 76 nets.

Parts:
C201, C203, C205, C206, C207, C304, C610: 10u; C_0805
C202, C204, C212, C601, C607, C608: 1u; C_0603
C208: 330p; C_0603
C209: 10p; C_0603
C210: 33p; C_0603
C211: 2.2u; C_0603
C301, C305, C307, C308, C609: 100n; C_0603
C302, C303: 25p; C_0603
C306: 100u; CP_Tantalum_Case-D_EIA-7343-31_Reflow
C602, C603: 100n 1%; C_0603
C605: 100n 1% DNP; C_0603
C611: 10n; C_0603
D301: SMD-LED-CLEAR-GREEN_0603_; LED-0603
D302: SMD-LED-CLEAR-BLUE_0603_; LED-0603
FID1, FID2, FID3: Fiducial_1mm_Dia_2.54mm_Outer_CopperTop
J201: BATT_CONN_01X02; TerminalBlock_Pheonix_PT-3.5mm_2pol
J301: CONN_01X04; Pin_Header_Straight_1x04
J402: CONN_01X05; TerminalBlock_Pheonix_MPT-2.54mm_5pol
J502: CONN_01X06; Pin_Header_Straight_1x06_Pitch2.54mm
J601: LOAD_CELL_CONN_01X04; TerminalBlock_Pheonix_MPT-2.54mm_4pol
J701: RFID_CONN_01X05; TerminalBlock_Pheonix_MPT-2.54mm_5pol
JP203: Jumper_3V3; GS2
JP501, JP502, JP503: Jumper; GS2
L201: 5uH; Inductor_Taiyo-Yuden_NR-60xx_HandSoldering
L202: 4.7uH; Inductor_Taiyo-Yuden_NR-30xx
L301: SMD-FERRITE-BEAD-2500R-50MA_0603_; L0603
P301: RX/TX; Socket_Strip_Straight_1x02_Pitch2.54mm
P302: TST/RST; Socket_Strip_Straight_1x02_Pitch2.54mm
P303: DEBUG_3V3; Socket_Strip_Straight_1x02_Pitch2.54mm
Q201: TPH1R712MDL1Q; TDSON-8-1_HandSoldering
Q301: NTR3A052PZT1G; TSOT-23
Q701: DMG3402L; TSOT-23
R201, R207, R208, R302, R507, R701, R704, R705: 82k; R_0603
R202, R301, R702, R703: 47k; R_0603
R203, R308, R309, R501, R503, R504, R505, R506: 10k; R_0603
R204: 162k 1%; R_0603
R205: 649k 1%; R_0603
R206: 15k; R_0603
R303, R304: 0R; R_0603
R306, R307: 1k; R_0603
R603, R604: 1k 1% --> short to 0R; R_0603
R605, R606: 100R 1%; R_0603
R607, R608: DNP; R_0603
R610, R611, R612: 47R; R_0603
SW201: external_button; SW_SPST_B3U-1000P
SW301: SMD-BUTTON_2P-3.0X2.5X1.2+0.4MM_; SW_SPST_B3S-1000
TP_RTC301: CONN_01X01; Socket_Strip_Straight_1x01_Pitch2.00mm
U201: TPS62745; WSON_3x2mm_12pin
U202: LTC3534; SSOP16-0.635-5X4MM
U203: LP5907; SOT23-5
U204: TPS73433DDCR; SOT23-5
U301: MSP430FR5969; S-PVQFN-N48
U501: ESP-12S; ESP-12E_SMD_UART_ONLY
U601: ADS1220; TSSOP-16_4.4x5mm_Pitch0.65mm
Y301: Crystal; X2-SMD-L2.0X1.2X0.55MM

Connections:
+3V3: C202.1, C304.2, C305.2, C306.1, C608.1, C609.2, JP203.2, L301.2, P303.1, Q301.2, R301.2, R302.1, R308.1, U203.1, U301.37, U601.13
+5V: C206.1, C207.1, J701.1, R203.2, R205.1, R701.2, U202.11
+BATT: C201.1, C203.1, Q201.3, SW201.1, U201.1, U201.8, U201.9, U201.10, U201.11, U201.12, U202.12, U202.13
/Communication/DTR: J502.1, R505.2, U501.12
/Communication/ESP12_ENABLE: J502.5, R503.1, U301.15, U501.3
/Communication/ESP12_RX: JP501.1, U301.24
/Communication/ESP12_TX: JP503.1, U301.25
/Communication/ESP12_VCC_sense: R507.2, TP_RTC301.1, U301.1
/Communication/RX: J502.3, JP501.2, U501.15
/Communication/TX: J502.2, JP503.2, U501.16
/Control/5V_ENABLE: R207.2, U202.2, U301.12
/Control/AVCC: C301.1, L301.1, U301.48
/Control/BAT_TEST_ENABLE: U201.4, U301.38
/Control/DBG_LED1: D301.+, U301.16
/Control/DBG_LED2: D302.+, U301.17
/Control/DBG_Switch: R308.2, R309.1, SW301.2, U301.18
/Control/HK_BAT_V: R201.1, R202.2, U301.39
/Control/LOADCELL_SPI_CS: U301.28, U601.2
/Control/RFID_CLK: R702.1, R704.2, U301.11
/Control/RFID_DATA: R703.2, R705.1, U301.19
/Control/RFID_SLEEP_N: Q701.1, U301.3
/Control/RX: P301.1, R304.1, U301.21
/Control/SD_CARD_ENABLE: Q301.1, R302.2, U301.14
/Control/SPI_CLK: R610.1, U301.26
/Control/SPI_MISO: R612.1, U301.32
/Control/SPI_MOSI: R611.1, U301.31
/Control/TX: P301.2, R303.1, U301.20
/Load_Cell/AIN1: C605.1, R603.1, U601.10
/Load_Cell/AIN2: C605.2, R604.1, U601.7
/Load_Cell/DRDY_N: U301.27, U601.14
/Load_Cell/EXC_A: C601.1, C602.1, J601.1, R605.2
/Load_Cell/EXC_B: C601.2, C603.1, J601.4, R606.2
/Load_Cell/conn2: J601.2, R604.2
/Load_Cell/conn3: J601.3, R603.2
/PIR_EN: J402.2, U301.2
/PIR_OUT1: J402.3, U301.4
/PIR_OUT2: J402.4, U301.5
/Power/5V_PWM: U202.10, U301.8
/Power/LDO_EN: R208.2, U203.3, U301.13
/Power/batt_in: J201.2, Q201.1
GND: C201.2, C202.2, C203.2, C204.2, C205.2, C206.2, C207.2, C211.2, C212.2, C301.2, C302.2, C303.2, C304.1, C305.1, C306.2, C307.2, C308.2, C602.2, C603.2, C608.2, C609.1, C610.1, C611.1, J201.1, J301.4, J402.5, J502.6, J701.5, P303.2, Q201.2, Q701.2, R202.1, R204.1, R207.1, R208.1, R306.2, R307.2, R504.1, R704.1, R705.2, SW301.1, U201.3, U201.GND1, U201.GND2, U202.1, U202.3, U202.4, U202.7, U202.8, U202.9, U202.16, U203.2, U204.2, U301.36, U301.41, U301.44, U301.47, U301.VSS_, U501.9, U601.3, U601.4, U601.5
unnamed: C205.1, JP203.1, L202.2, U201.5
unnamed: C208.1, R206.1
unnamed: C208.2, C209.2, U202.14
unnamed: C209.1, C210.2, R204.2, R205.2, R206.2, U202.15
unnamed: C210.1, R203.1
unnamed: C212.1, SW201.2, U204.1, U204.3
unnamed: C302.1, U301.46, Y301.1
unnamed: C303.1, U301.45, Y301.2
unnamed: C307.1, J301.3, Q301.3
unnamed: C308.1, R309.2
unnamed: C607.2, R606.1, R607.2, U601.6
unnamed: D301.-, R306.1
unnamed: D302.-, R307.1
unnamed: J301.1, R303.2
unnamed: J301.2, R304.2
unnamed: J701.2, R702.2
unnamed: J701.3, R703.1
unnamed: J701.4, Q701.3, R701.1
unnamed: JP502.2, R507.1
unnamed: L201.1, U202.5
unnamed: L201.2, U202.6
unnamed: L202.1, U201.2
unnamed: P302.1, R301.1, U301.23
unnamed: P302.2, U301.22
unnamed: R201.2, U201.6
unnamed: R501.2, U501.1
unnamed: R504.2, U501.10
unnamed: R506.2, U501.11
unnamed: R607.1, U601.9
unnamed: R608.1, U601.8
unnamed: R610.2, U601.1
unnamed: R611.2, U601.16
unnamed: R612.2, U601.15
VAA: C204.1, C607.1, C610.2, C611.2, R605.1, R608.2, U203.5, U601.11, U601.12
VDDA: C211.1, J402.1, J502.4, JP502.1, R501.1, R503.2, R505.1, R506.1, U204.5, U501.8

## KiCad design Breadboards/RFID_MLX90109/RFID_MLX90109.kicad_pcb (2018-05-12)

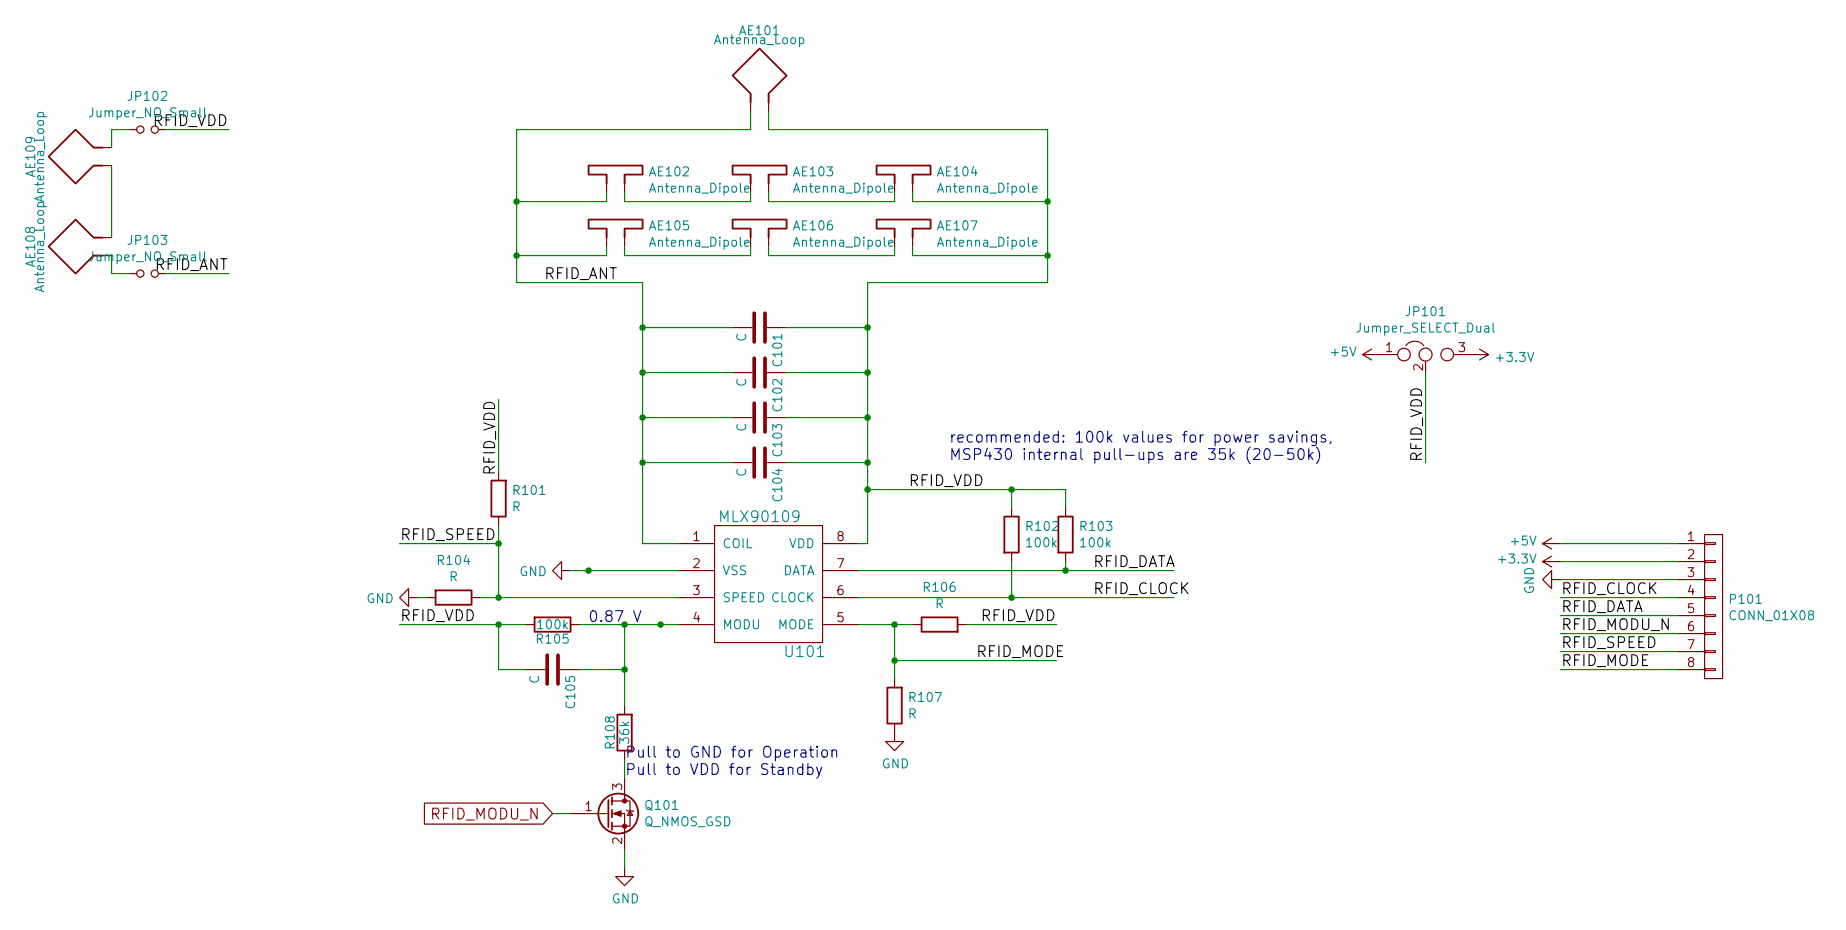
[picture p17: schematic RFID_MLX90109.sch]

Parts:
AE101: Antenna_Loop; R_Axial_DIN0411_L9.9mm_D3.6mm_P25.40mm_Horizontal
AE102, AE103, AE104, AE105, AE106, AE107: Antenna_Dipole; TDK_B82450A
AE108, AE109: Antenna_Loop; 125kHz_PCB_Antenna
C101, C102: C; C_Rect_L7.0mm_W3.5mm_P5.00mm
C103, C104, C105: C; C_0805_HandSoldering
JP101: Jumper_SELECT_Dual; Pin_Header_Straight_1x03_Pitch2.54mm
JP102, JP103: Jumper_NO_Small; Pin_Header_Straight_1x02_Pitch2.54mm
P101: CONN_01X08; Pin_Header_Straight_1x08_Pitch2.54mm
Q101: Q_NMOS_GSD; SOT-23_Handsoldering; Mouser-Part 726-BSS127H6327
R101, R104, R106, R107: R; R_0603_HandSoldering
R102, R103, R105: 100k; R_0603_HandSoldering
R108: 36k; R_0603_HandSoldering
U101: MLX90109; SOIC-8_3.9x4.9mm_Pitch1.27mm

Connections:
+3V3: JP101.3, P101.2
+5V: JP101.1, P101.1
/RFID_ANT: AE101.1, AE102.1, AE105.1, C101.2, C102.2, C103.2, C104.2, JP103.2, U101.1 (COIL)
/RFID_CLOCK: P101.4, R102.2, U101.6 (CLOCK)
/RFID_DATA: P101.5, R103.2, U101.7 (DATA)
/RFID_MODE: P101.8, R106.1, R107.2, U101.5 (MODE)
/RFID_SPEED: P101.7, R101.1, R104.1, U101.3 (SPEED)
/RFID_VDD: AE101.2, AE104.2, AE107.2, C101.1, C102.1, C103.1, C104.1, C105.2, JP101.2, JP102.2, R101.2, R102.1, R103.1, R105.2, R106.2, U101.8 (VDD)
GND: P101.3, Q101.2 (S), R104.2, R107.1, U101.2 (VSS)
unnamed: AE102.2, AE103.1
unnamed: AE103.2, AE104.1
unnamed: AE105.2, AE106.1
unnamed: AE106.2, AE107.1
unnamed: AE108.1, JP103.1
unnamed: AE108.2, AE109.2
unnamed: AE109.1, JP102.1
unnamed: C105.1, R105.1, R108.2, U101.4 (MODU)
unnamed: Q101.3 (D), R108.1
RFID_MODU_N: P101.6, Q101.1 (G)

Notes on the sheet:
Pull to GND for Operation Pull to VDD for Standby
0.87 V
recommended: 100k values for power savings, MSP430 internal pull-ups are 35k (20-50k)

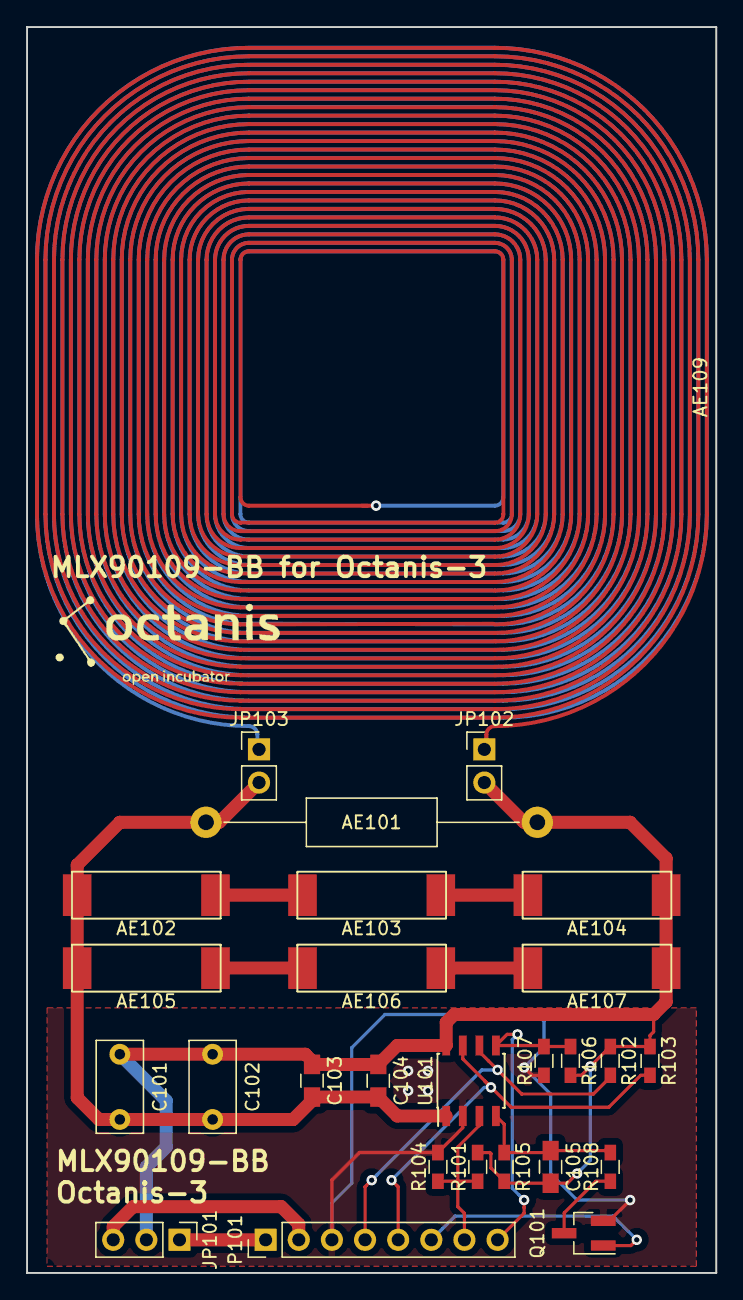
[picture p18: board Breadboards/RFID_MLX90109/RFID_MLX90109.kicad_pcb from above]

Board: 2 copper layers, 52.8 x 95.5 mm, 28 parts (1 on the bottom side), 19 nets.

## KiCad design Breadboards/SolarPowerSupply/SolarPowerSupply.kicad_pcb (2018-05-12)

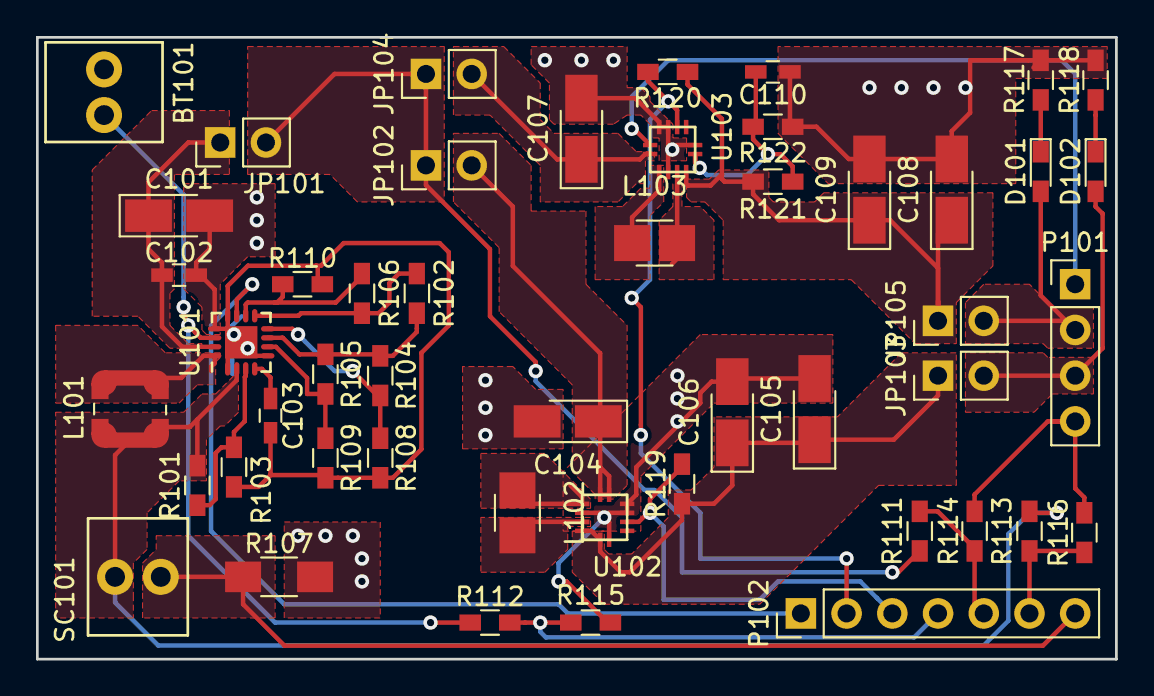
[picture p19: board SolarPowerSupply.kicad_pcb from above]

Board: 2 copper layers, 59.9 x 34.5 mm, 49 parts (0 on the bottom side), 34 nets.

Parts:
BT101: Battery; TE_282834-2
C101: 4.7u; C_SMD_2012_Hand
C102: 100n; C_0603_HandSoldering
C103: 10n; C_0603_HandSoldering
C104, C105, C106, C107, C108, C109: 10u; C_SMD_2012_Hand
C110: 10p; C_0603_HandSoldering
D101, D102: LED; LED_0603_HandSoldering
JP101, JP102, JP103, JP104, JP105: Jumper; Pin_Header_Straight_1x02_Pitch2.54mm
L101: 22u; L_Wuerth_WE-TPC-3816
L102, L103: 1.5u; L_2520_HandSoldering
P101: CONN_01X04; Pin_Header_Straight_1x04_Pitch2.54mm
P102: CONN_01X07; Pin_Header_Straight_1x07_Pitch2.54mm
R101, R102, R103, R104, R105, R106, R108, R109, R110, R111, R112, R113, R114, R115, R116, R117, R118, R121, R122: R; R_0603_HandSoldering
R107: 1E; R_1206_HandSoldering
R119, R120: 1M; R_0603_HandSoldering
SC101: Solar_Cells; TE_282834-2
U101: bq25504; QFN-16-1EP_3x3mm_Pitch0.5mm
U102: TPS63051; VQFN_12_2.5x2.5mm
U103: TPS63050; VQFN_12_2.5x2.5mm

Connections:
5V_Enable: P101.1, U103.11
+3V3: D102.2, JP103.2, P101.3
+5V: D101.2, JP105.2, P101.2
/VBat: BT101.1, R112.1, U101.14
/VBus: JP101.2, JP102.1, JP104.1, R111.1
/VSolar: L101.1, R101.1, R113.1, SC101.1, U101.2
BAT_OK: P102.1, U101.11
GND: BT101.2, C101.2, C102.2, C103.2, C104.2, C105.2, C106.2, C107.2, C108.2, C109.2, C110.2, P101.4, R103.2, R107.2, R108.2, R109.2, R110.2, R114.2, R115.2, R116.2, R117.2, R118.2, R122.1, U101.1, U101.5, U101.12, U101.13, U101.17, U102.2, U102.6, U102.9, U102.10, U103.2, U103.6, U103.9, U103.10
HK_BAT_V: P102.4, R112.2, R115.1
HK_BUS_V: P102.5, R111.2, R114.1
HK_SOLAR_I: P102.7, R107.1, SC101.2
HK_SOLAR_V: P102.6, R113.2, R116.1
unnamed: C101.1, C102.1, JP101.1, U101.15
unnamed: C103.1, U101.4
unnamed: C104.1, JP102.2, U102.11, U102.12
unnamed: C105.1, C106.1, JP103.1, R119.1, U102.4, U102.5
unnamed: C107.1, JP104.2, U103.12
unnamed: C108.1, C109.1, JP105.1, R120.1, R121.1, U103.4
unnamed: C110.1, R121.2, R122.2, U103.5
unnamed: D101.1, R117.1
unnamed: D102.1, R118.1
unnamed: L101.2, U101.16
unnamed: L102.1, U102.1
unnamed: L102.2, U102.3
unnamed: L103.1, U103.1
unnamed: L103.2, U103.3
unnamed: R101.2, R103.1, U101.3
unnamed: R102.1, R104.1, R105.1, U101.7
unnamed: R102.2, R106.1, U101.9
unnamed: R104.2, R108.1, U101.8
unnamed: R105.2, R109.1, U101.6
unnamed: R106.2, R110.1, U101.10
PGOOD_3.3: P102.3, R119.2, U102.8
PGOOD_5: P102.2, R120.2, U103.8

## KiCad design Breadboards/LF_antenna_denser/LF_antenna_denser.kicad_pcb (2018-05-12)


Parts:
AE1, AE2: Antenna_Loop; 125kHz_PCB_Antenna_wide
R_ant1: R; Resistor_Horizontal_RM25mm

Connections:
unnamed: AE1.1, AE2.1
unnamed: AE1.2, R_ant1.2
unnamed: AE2.2, R_ant1.1


Board: 2 copper layers, 90.0 x 64.0 mm, 3 parts (1 on the bottom side), 3 nets.

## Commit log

2017-01-17 Initial commit; Finished schematic for microcontroller, RFID reader IC, DC-DC converter and light barrier. Assigned all footprints to schematic symbols. Now we can start layouting
    [Nestbox_v1.kicad_pcb, Nestbox_v1.sch, nestbox_Reader_IC.sch, nestbox_power.sch]
2017-02-05 pcb file components clustering
    pcb file components were clustered according to the Eeschema -
    currently everything is on one layer, F.Cu
    [Nestbox_v1.kicad_pcb, Nestbox_v1.sch, nestbox_Reader_IC.sch, nestbox_power.sch]
2017-03-03 circular NFC antenna added to pcb file, as well as other important changes and additions of library components
    [Nestbox_v1.kicad_pcb, Nestbox_v1.sch, nestbox_Reader_IC.sch, nestbox_power.sch]
2017-03-03 corrected antenna pin orientation
    [Nestbox_v1.kicad_pcb]
2017-03-03 NFC & power placed
    [Nestbox_v1.kicad_pcb, nestbox_power.sch]
2017-03-03 added lora component
    [Nestbox_v1.kicad_pcb, Nestbox_v1.sch, nestbox_Reader_IC.sch, nestbox_lora.sch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]
2017-03-03 finished component placement incl. LoRa
    [Nestbox_v1.kicad_pcb, Nestbox_v1.sch, nestbox_lora.sch]
2017-03-03 board outline
    [Nestbox_v1.kicad_pcb]
2017-03-04 added additional connector for light barrier
    [Nestbox_v1.kicad_pcb, Nestbox_v1.sch, nestbox_lora.sch]
2017-03-06 corrected phototransistor pins, added power jumpers & testpoints and light barrier signal access
    [Nestbox_v1.kicad_pcb, Nestbox_v1.sch, nestbox_Reader_IC.sch, nestbox_lora.sch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]
2017-03-06 added second phototransistor. started routing power and analog traces
    [Nestbox_v1.kicad_pcb, Nestbox_v1.sch, nestbox_Reader_IC.sch, nestbox_lora.sch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]
2017-03-07 finished big part of the routing
    [Nestbox_v1.kicad_pcb, _saved_Nestbox_v1.sch]
2017-03-07 routing done. missing: top ground plane, stitching vias
    [Nestbox_v1.kicad_pcb]
2017-03-07 added schematic changes
    [Nestbox_v1.sch, _saved_Nestbox_v1.sch, nestbox_Reader_IC.sch, nestbox_lora.sch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]
2017-03-08 silk screen, stitching, top gnd plate
    [Nestbox_v1.kicad_pcb]
2017-03-08 corrected gnd vias, added logo footprints
    [Nestbox_v1.kicad_pcb]
2017-03-08 added logo
    [Nestbox_v1.kicad_pcb]
2017-03-08 generated gerber files
    [Nestbox_v1-B.Cu.gbl, Nestbox_v1-B.Mask.gbs, Nestbox_v1-B.SilkS.gbo, Nestbox_v1-Edge.Cuts.gm1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]
2017-03-20 corrected solder mask expansion and generated paste gerber file
    [Nestbox_v1-F.Mask_stencil.gtp, Nestbox_v1.kicad_pcb]
2017-03-24 created BOM
    [Nestbox_v1.csv]
2017-03-25 created component library with completed MPN
    [Nestbox_v1_component_library.csv]
2017-03-25 updated schematics and BOM with MPN
    [Nestbox_v1.csv, Nestbox_v1.sch, Nestbox_v1_individual.csv, nestbox_Reader_IC.sch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]
2017-04-04 Updated BOM with correct light barrier values
    [Nestbox_v1.csv, Nestbox_v1.sch, Nestbox_v1_matching_network.xlsx, nestbox_Reader_IC.sch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]
2017-04-08 Updated BOM with one version of the antenna matching network components
    [Nestbox_v1.csv, Nestbox_v1.sch, nestbox_Reader_IC.sch, nestbox_lora.sch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]
2017-04-08 added feedback of first soldering round (3pcs)
    [Issues_PCBv1.ods, Nestbox_v1.sch]
2017-10-24 Restuctured the folder for Nestbox_v2 PCB
    - Moved all Nestbox_v1 files to subfolder "Nestbox_v1"
    - Created folder for administrative documents "_admin"
    - Updated Nestbox_v1.pro KICAD project to use relative paths for
    libraries
    - Updated README.md to reflect new folder structure
    [Issues_PCBv1.ods, Nestbox_v1-B.Cu.gbl, Nestbox_v1-B.Mask.gbs, Nestbox_v1-B.SilkS.gbo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]
2017-10-24 Init Nestbox_v2 KICAD project
    - Created new KICAD project for Nestbox_v2
    - Linked to existing libraries
    [Nestbox_v2.kicad_pcb, Nestbox_v2.sch]
2017-10-24 Started drawing schematic: RFID part
    - Structured the complete schematic into 4 subschematics:
    - Power: Power supply
    - Control: MSP430
    - RFID: MLX90109 and antenna
    - Passage Detector: Light barrier, IR sensor etc.
    - Draw RFID schematic according to Section 9.1 of the MLX90109 user
    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
    [Nestbox_v2_RFID.sch, Nestbox_v2_control.sch, Nestbox_v2_detector.sch, Nestbox_v2_power.sch]
2017-10-24 updated pcb v1 (?)
    [Nestbox_v1.kicad_pcb]
2017-10-25 Includes MSP430 design based on Nestbox_v1
    The MSP430 controller as included in the Nestbox_v1 has been integrated
    into the Nestbox_v2_control sheet.
    Proper connections have not yet been established.
    [Nestbox_v2.sch, Nestbox_v2_RFID.sch, Nestbox_v2_control.sch, Nestbox_v2_detector.sch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]
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2017-10-29 Integrates the power supply circuit.
    The power supply circuit (3.3V regulator is copied from the NestboxV1 and
    integrated into the current design.
    [Nestbox_v2.sch, Nestbox_v2_RFID.sch, Nestbox_v2_control.sch, Nestbox_v2_detector.sch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]
2017-10-29 Adds a LORA schame
    The LORA schema is copied from the previous Nestbox V1 schmeatic.
    [Nestbox_v2.sch, Nestbox_v2_LORA.sch, Nestbox_v2_RFID.sch, Nestbox_v2_control.sch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]
2017-10-29 Corrects RFID global labels
    The lables used in the RFID sheet were local labels so far. These have been
    replaced with global labels, to allow the interconnection with the MSP.
    [Nestbox_v2_RFID.sch]
2017-11-03 Modifies RFID circuit
    - Correctly calculate resistive divider to get 0.9 V from 3.3
    - Hardwire speed input
    - Connect MODU to global label (to MSP430)
    - Annotate schematic
    [Nestbox_v2_RFID.sch]
2017-11-03 Connects global signals to MSP430
    - Connect SPI signals for SD-Card
    - Connect RFID signals for MLX
    - Connect ADC signals for housekeeping
    - Connect Lightbarrier signals
    [Nestbox_v2_control.sch]
2017-11-03 Renames LORA schema to Comm
    As multiple communication protocol could be included, renamed the LORA
    schematic to a more general Comm schematic.
    [Nestbox_v2.sch, Nestbox_v2_Comm.sch, Nestbox_v2_LORA.sch]
2017-11-03 Adds SD card to Control schematic
    SD card schematic symbol has been added and connected.
    [Nestbox_v2_control.sch]
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2017-11-04 Adds schamtic of light barriers
    - Light barriers using SFH4656 as emitter and RSOP38 as detector.
    - Includes separate Connector to solder remote LED
    [Nestbox_v2_detector.sch]
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2017-11-04 Adds XBee module to Communication schematic
    The XBee module would be used for local data transfer, from a Nestbox to a
    computer. This would allow data readout without the need to physically access
    the box.
    [Nestbox_v2_Comm.sch]
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2017-11-05 Replaces R and C in control schematic with std comp
    The R and C components used in the controll schematic where replaced with standard components
    [Nestbox_v2_control.sch]
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2017-11-07 VDD select jumper added to RFID part
    The VDD for the RFID chip can now be chosen between 5V and 3.3V using a
    jumper.
    TODO: Check the correct voltage levels for the MODU pin.
    [Nestbox_v2_RFID.sch]
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2017-12-03 Modified layout around bq25504
    In order to be more in accordance with the layout guidelines as listed in the
    bq25504 datasheet, the layout around the mentioned chip was reworked.
    Mainly the CStor and CBypass as well as the inductor were replaced.
    The pouring of ground and supply planes was also redone.
    [SolarPowerSupply.kicad_pcb]
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2017-12-03 Ensures Design mostly DRC clean
    Removed remaining DRC errors, mostly copper traces too close.
    Some DRC errors remain, within the SOIC-16 package of the bq25504,
    "PADS TOO CLOSE" -> to be ignored.
    [SolarPowerSupply.kicad_pcb, SolarPowerSupply.sch]
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2018-01-02 Changes CREF to low leakage capacitor
    The 10nF CREF capacitor used by the bq25504 needs to be of low leakage quality,
    as it needs to hold the input voltage reference for up to 16s. With the current
    capacitor (no-name) the voltage drops by approx. 25% during these 16s.
    [SolarPowerSupply.sch]
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2018-05-30 correct size of the PCB drawn with connector arrangement done as well
    [Load_Cell.sch, Nestbox_v2.kicad_pcb, Nestbox_v2_Comm.sch, Nestbox_v2_RFID.sch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]
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2018-06-04 ESP footprint to the essential and broke out programming pins
    [Nestbox_v2.kicad_pcb, Nestbox_v2.sch, Nestbox_v2_Comm.sch]
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2018-06-07 corrected transistor pins
    [Load_Cell.sch, Nestbox_v2-B.Cu.gbl, Nestbox_v2-B.Mask.gbs, Nestbox_v2-B.Paste.gbp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]
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2018-06-07 generated correct GERBER files - ORDERED june 7
    [nestbox-B.Cu.gbr, nestbox-B.Mask.gbr, nestbox-B.Paste.gbr, nestbox-B.SilkS.gbr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]
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2018-06-13 second PCB for EM4095 and created fabrication files of main board and corrected holes locations
    [Nestbox_v2-B.Cu.gbl, Nestbox_v2-B.Mask.gbs, Nestbox_v2-B.Paste.gbp, Nestbox_v2-B.SilkS.gbo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]
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2018-06-21 TAPEOUT second batch nestbox main + EM pcb. added pull-ups, corrected pmos of load cell, WIFI AND SDCARD ENABLE PMOS ARE STILL WRONGLY ORIENTED
    [Load_Cell.sch, Nestbox_v2-B.Cu.gbl, Nestbox_v2-B.Mask.gbs, Nestbox_v2-B.Paste.gbp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]
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2018-10-20 removed any unnecessary functions and connectors. corrected transistor bug
    [Load_Cell.sch, Nestbox_v2_Comm.sch, Nestbox_v2_detector.sch]
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
